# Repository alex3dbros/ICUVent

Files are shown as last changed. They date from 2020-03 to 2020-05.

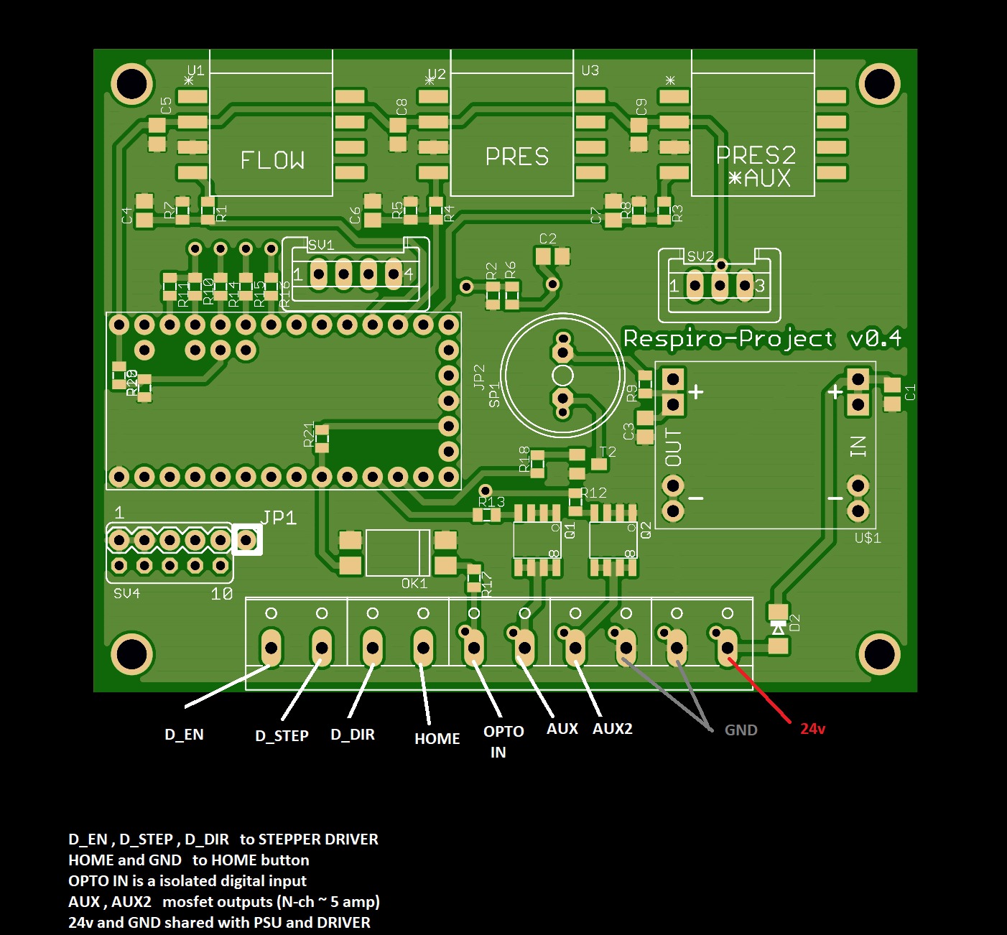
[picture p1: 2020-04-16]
Hardware/pinout.jpeg

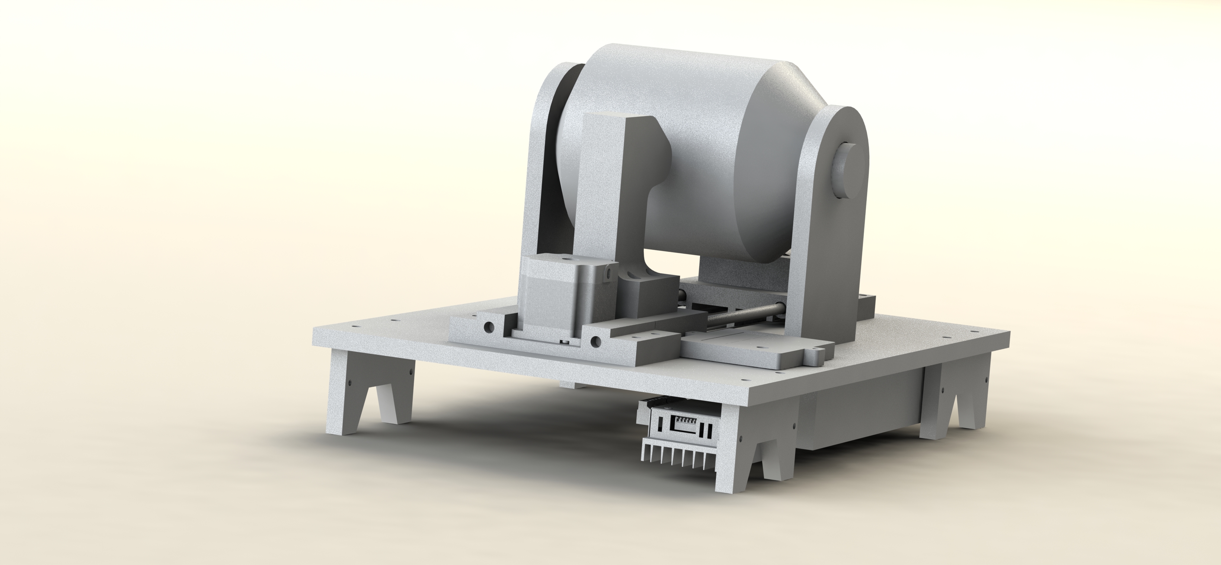
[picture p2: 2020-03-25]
3DModels/Render2.JPG

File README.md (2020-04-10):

# ICUVent

Video Overview: https://youtu.be/w7vbeYg_BhQ

This project is opensource and there are no guarantees given that this device 
will perform the actions that it's needed to be. Please use it with care and 
under the surveilance of professionals.

Project Structure:

Inside 3DModels folder you have the solidworks 2019 and STL files 
Inside programming you will have the programming code used to control the device.
We started with Arduino Nano, stepper Driver and nema 23 motor.

You have the schematics of the circuit attached as well.

Parts used that must be purchased: 

Mechanics:
4 x 8mm round bearings from 3d printer
2 x 8mm rods
1 x Nema 34 Motor // Updated from nema 23, will update the design soon.
1 x 16 mm T5 belt
2 x 18 teeth T5 gear
1 x Ambubag, preferable with PEEP valve and safety valve

Electronics: 
1 x Teensy 3.2
1 x Driver PSD8079-2P
1 x Encoder like this : https://www.amazon.com/Cylewet-Encoder-Digital-Potentiometer-Arduino/dp/B07DM2YMT4/ref=sr_1_6?keywords=encoder&qid=1585150874&sr=8-6
1 x DC to DC 24V to 5V like this : https://www.amazon.com/6-5-28V-MP1584-DC-DC-Step-Down-Module/dp/B082957QHR/ref=sr_1_3?keywords=MP1584+5V&qid=1585150582&sr=8-3
1 x 24 V Power supply
1 x EndStop switch
1 x raspberry pi with 7 inch display
1 x MPXV5004DP
1 x MPXV5010DP

Connection pins - https://www.amazon.com/Hotop-Pack-Single-Header-Connector/dp/B06XR8CV8P/ref=sr_1_1?keywords=2.54+pins&qid=1585151123&sr=8-1&swrs=BA6CC27AC84D7760BA1186A07738C3A9

https://www.amazon.com/DEYUE-Jumper-Wires-Set-breadboard/dp/B07LFCLMGW/ref=sr_1_10?keywords=jumper+wires&qid=1585151157&sr=8-10

Connection wires

Some info about how I built it:

I 3D printed parts and cut at the CNC the larger ones.
Here's a video with the machine functional

All the best!

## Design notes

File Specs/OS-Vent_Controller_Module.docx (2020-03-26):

Open Source Ventilator

Controller Module

V1.0; Sem Lampotang, March 17, 2020; Department of Anesthesiology, Center for Safety, Simulation & Advanced Learning Technologies, University of Florida, Gainesville, Florida, USA

This module is essentially a timer that turns two valves on or off. When the inspiratory valve is open, the exhalation valve is closed and vice versa.

Respiratory rate (RR) = Number of breaths per minute (bpm)

Breath duration = 60 s/RR; e.g., for 10 bpm, breath duration = 60/10 = 6 s

Inspiratory:Expiratory time ratio (I:E ratio) = 1:2 (usually)

Inspiratory time (Ti; time in seconds spent in inspiration phase) = breath duration / (1 + I:E) = 6/(1+2) = 6/3 = 2 seconds

Expiratory time (Te; time in seconds spent in exhalation phase) = breath duration – inspiratory time = 6 - 2 = = 4 seconds

Tidal volume (VT) = volume of gas (ml) delivered during inspiration

For a constant flow inspiration, the flow rate to the patient is VT/(inspiratory time)

Input | Data Output | Physical output | Status
User selects tidal volume (see General Engineering Specifications) | | Gas flows towards patient during the selected inspiratory time
| | In constant flow design, gas flows to patient at a flow rate of VT/
User selects respiratory rate (see General Engineering Specifications) | Time when inspiration starts and ends | Time when gas starts flowing to patient Time when gas stops flowing to patient | Not claimed; No one working on it yet
| Time when exhalation starts and ends | Time when gas starts flowing from patient Time when gas stops flowing from patient | No one working on it yet ; No one working on it yet
Electromechanical design (no software)
User selects respiratory rate (see General Engineering Specifications) | Time when inspiration starts and ends | 12 V delivered to inspiratory valve 0 V to exhalation valve | No one working on it yet ; No one working on it yet
| Time when exhalation starts and ends | 12 V delivered to exhalation valve 0 V to inspiratory valve | No one working on it yet ; No one working on it yet
Electromechanical design (software)
User selection for tidal volume and respiratory rate (see General Engineering Specifications) | Variable “INSPIRATORY_VALVE_ON” is true when inspiration starts “INSPIRATORY_VALVE_ON” is false when inspiration ends | 12 V delivered to inspiratory valve 0 V to exhalation valve | No one working on it yet ; No one working on it yet
| Variable “EXHALATION_VALVE_ON” is true when exhalation starts “EXHALATION_VALVE_ON” is false when exhalation ends | 12 V delivered to exhalation valve 0 V to inspiratory valve | No one working on it yet ; No one working on it yet
Pneumatic Design – May require specialized parts that may be out of stock

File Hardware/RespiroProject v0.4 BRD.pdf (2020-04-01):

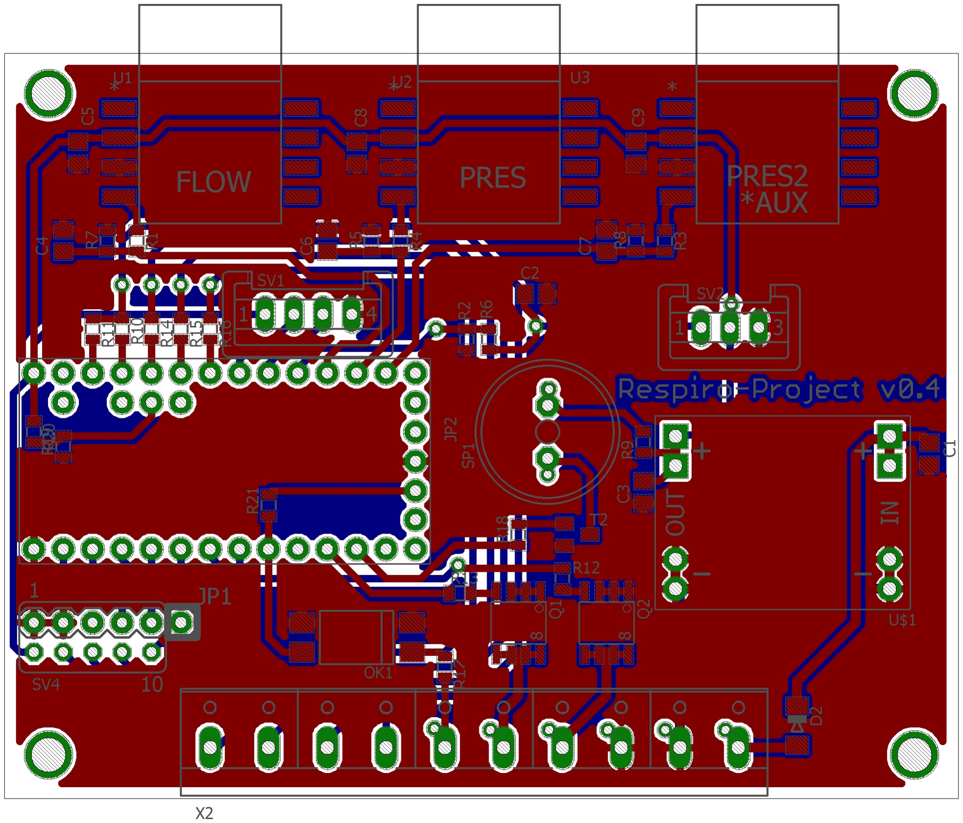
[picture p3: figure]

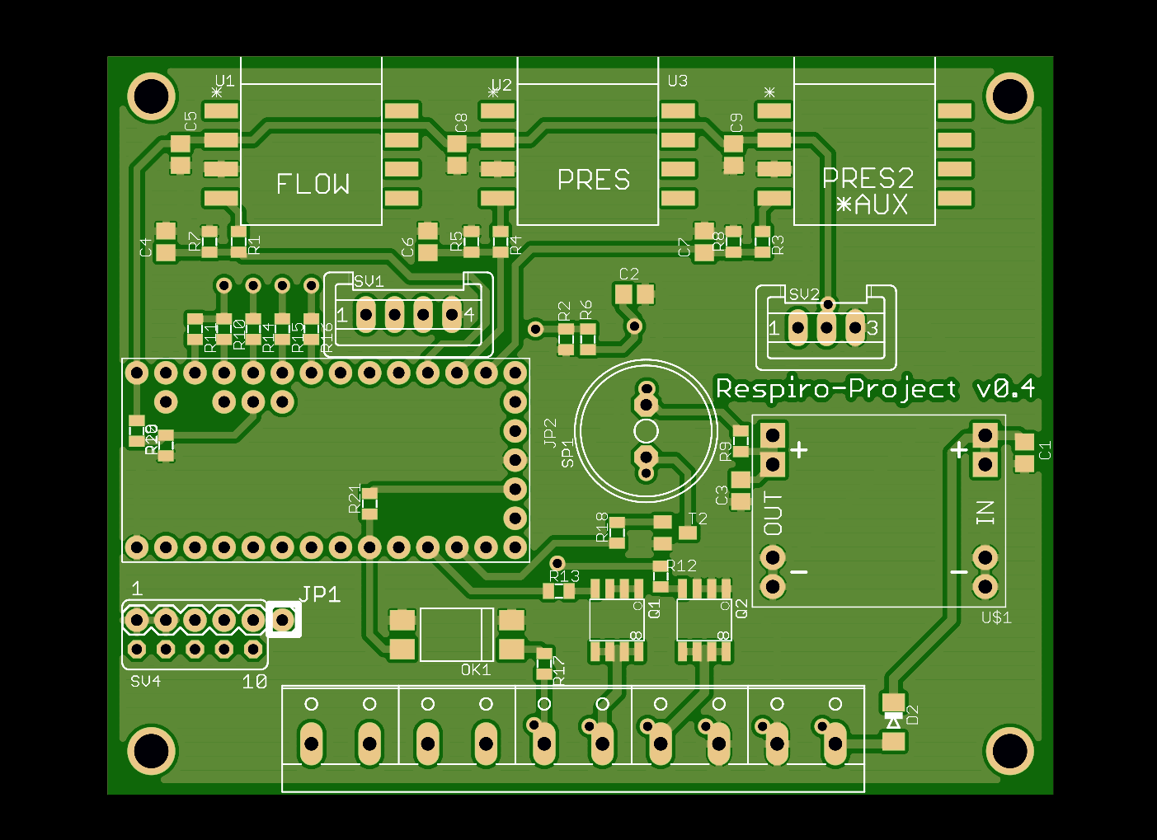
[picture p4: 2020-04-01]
Hardware/PCBPreview.png

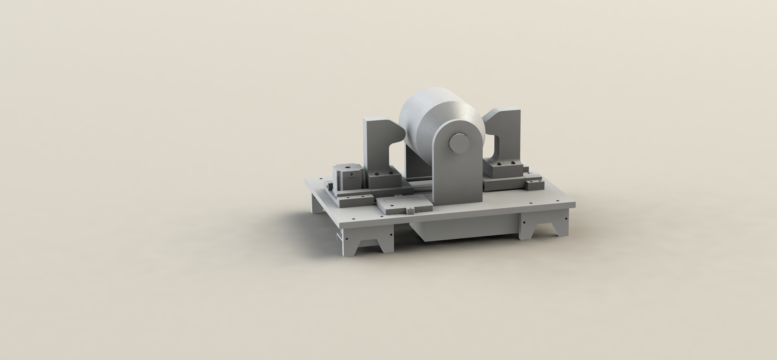
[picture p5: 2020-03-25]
3DModels/Render.JPG

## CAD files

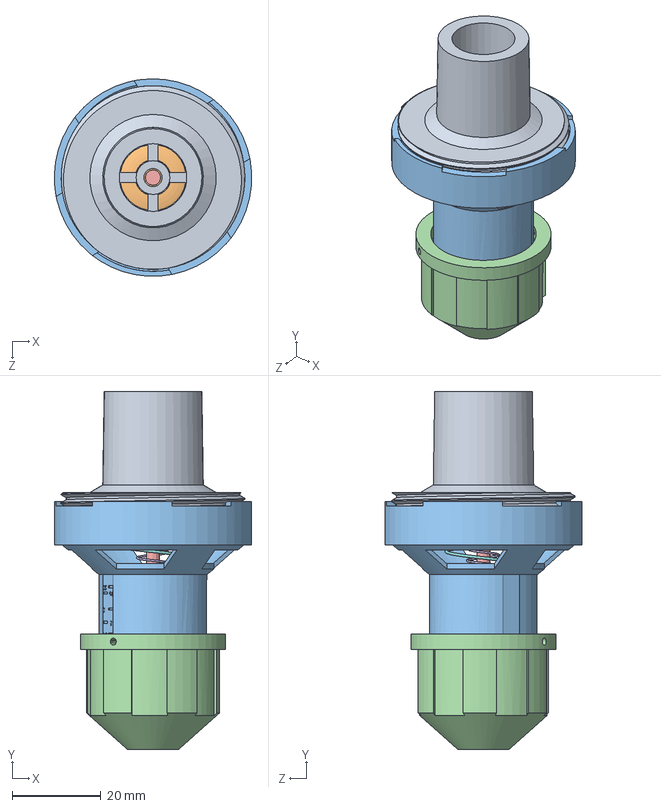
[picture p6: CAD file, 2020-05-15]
3DModels/Solidworks/ambu-bag-assembly-1.snapshot.2/Assy_PEEP_Valve.SLDASM
44.4 x 80.5 x 44.4 mm
PEEP_Body_Non_Adjustment
PEEP_Valve_Large_Silicone_Seal
PEEP_Body_Adjustment_Side
PEEP_Adjustment_Knob
PEEP_Pin_Center
PEEP_Spring_Taper
Platic_Float
PEEP_Spring_Large

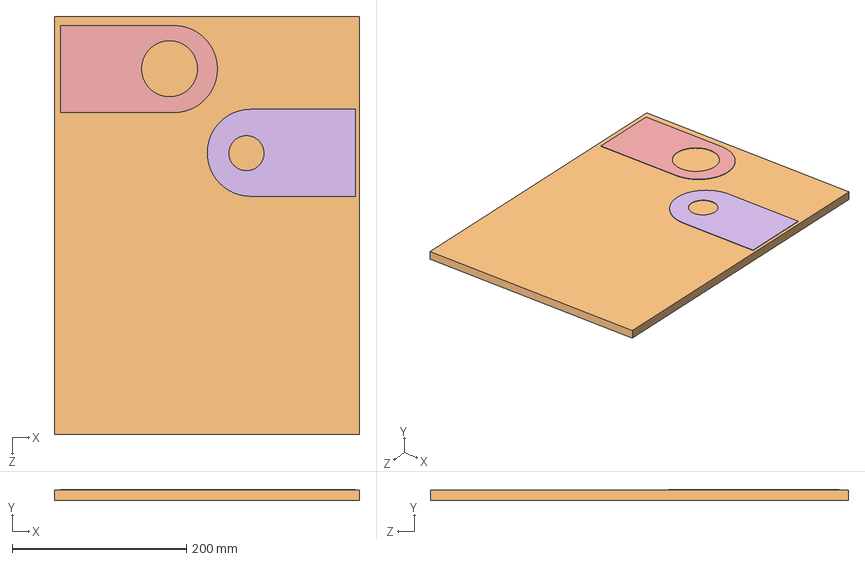
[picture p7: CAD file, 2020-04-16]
3DModels/Solidworks/CNC Cutting/CuttingParts_01.SLDASM
350.0 x 12.6 x 480.0 mm
MotorSupportNema34 x 4
StockMaterial
rolling_cnc_version x 4
GearSupport x 4
BagSupport1
BagSupport2

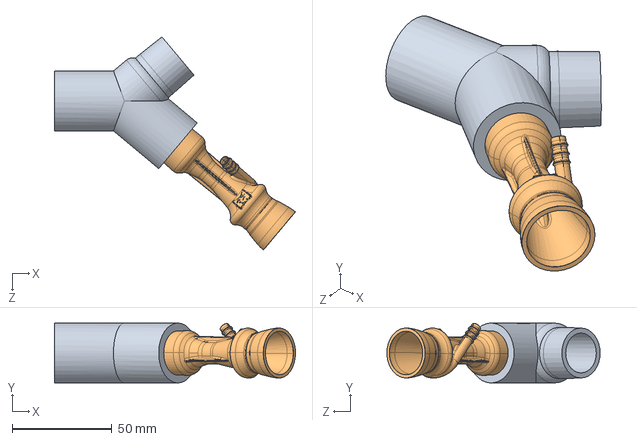
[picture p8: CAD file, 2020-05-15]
3DModels/Solidworks/Oxygen Mixing/Assem1.SLDASM
120.7 x 30.0 x 106.8 mm
Y_Oxygen_Connector
Respirator-free reanimation Venturi's valve (rev. 4) FiO2-40 Vertical, 1-piece

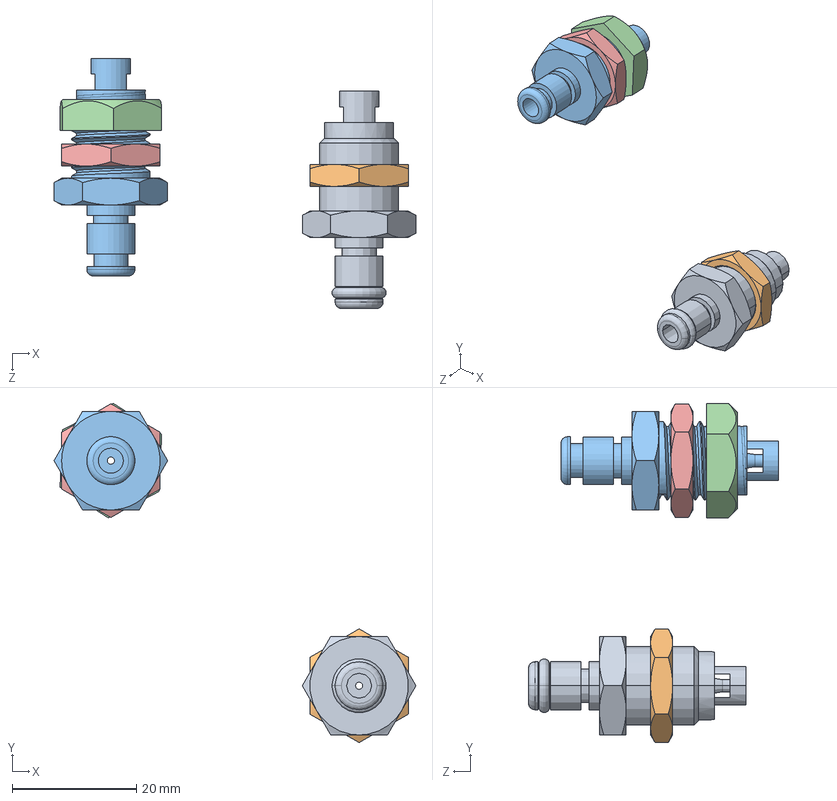
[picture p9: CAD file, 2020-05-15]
Fan Version/3D Models/Connectors/COLDER_PMC4201/SOLIDWORKS/PMC4201.sldasm
58.3 x 54.7 x 40.3 mm
_PMC4201_BODY_2
Nut
Nut2

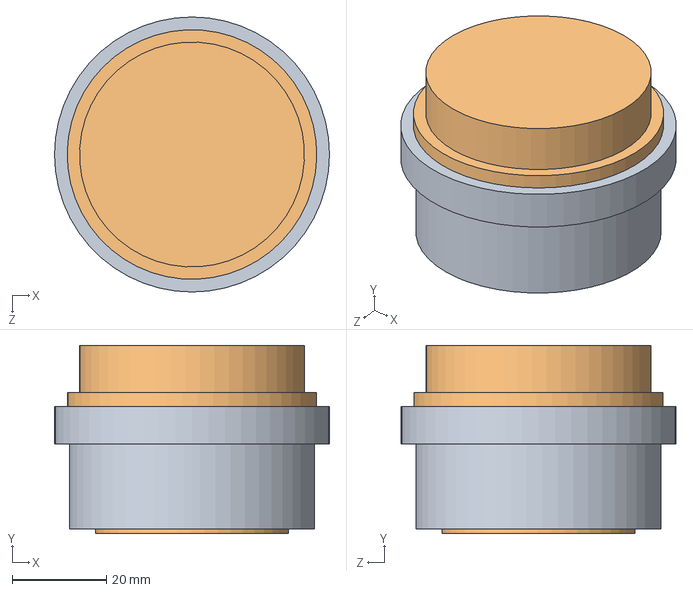
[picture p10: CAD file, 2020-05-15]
Fan Version/3D Models/Connectors/O2/O2.SLDASM
58.4 x 40.0 x 58.4 mm
O2Screw
R-30VSLDPRT

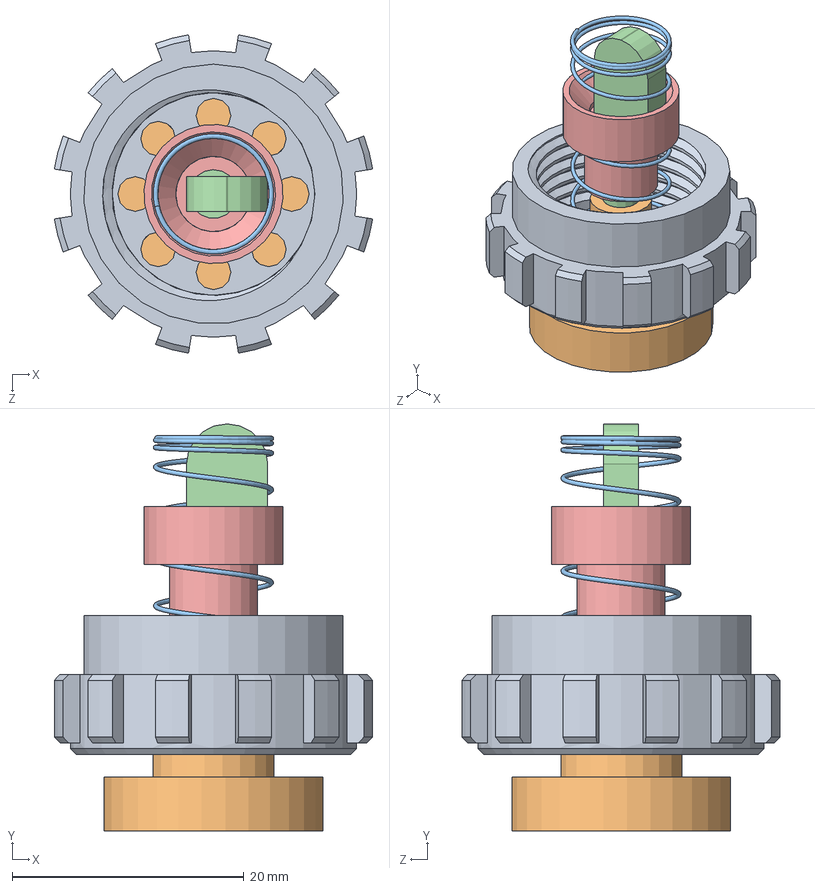
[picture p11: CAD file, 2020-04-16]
3DModels/Solidworks/ambu-bag-assembly-1.snapshot.2/Assy_Pressure_Relief_Valve.SLDASM
27.5 x 35.1 x 27.5 mm
Pressure Relief Valve Body
Pressure Relief Valve Pop_Up
Pressure Relief Valve Spring
Pressure Relief Valve Pin Center
Pressure Relief Valve Seal

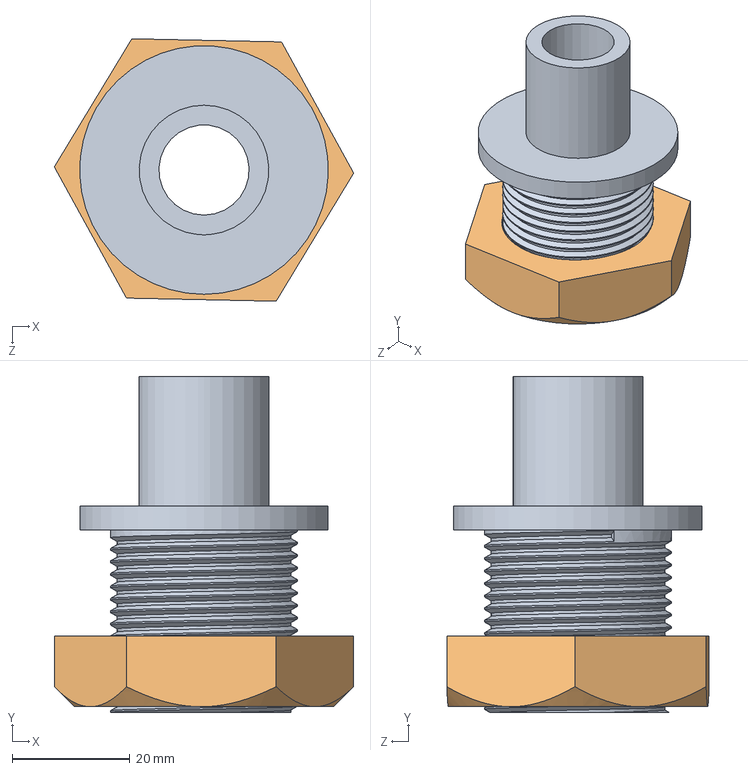
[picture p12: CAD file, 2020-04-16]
3DModels/Solidworks/OutputConnector.SLDASM
50.8 x 57.0 x 44.5 mm
OutputConnector-Screw
OutputConnector-Nut

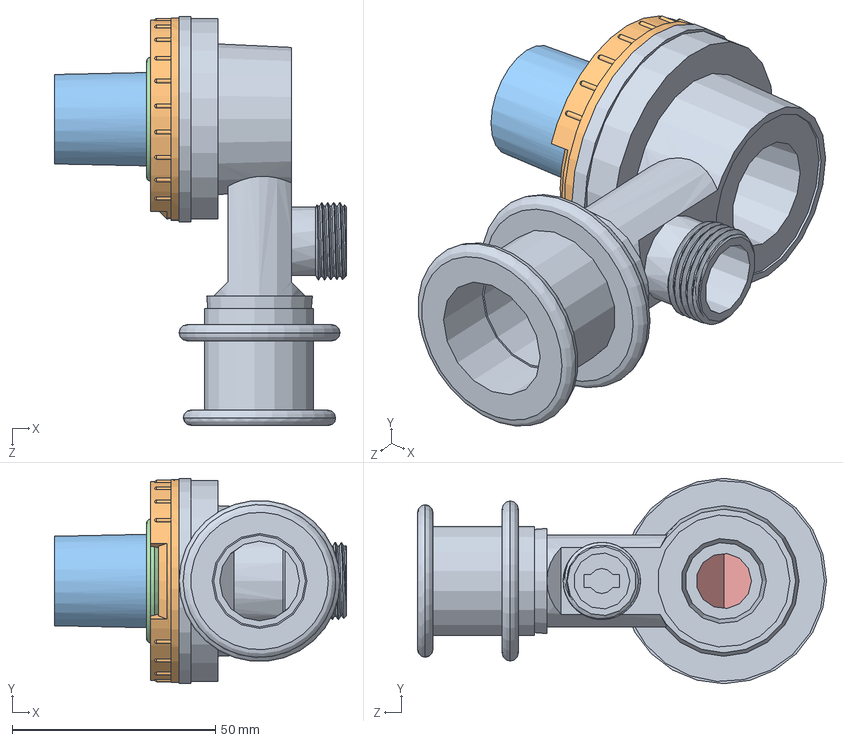
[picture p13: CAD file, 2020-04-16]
3DModels/Solidworks/ambu-bag-assembly-1.snapshot.2/Assy_Ambu-Bag_Outlet.SLDASM
71.8 x 50.5 x 100.6 mm
Ambu-Bag_Outlet
Ambu-Bag_Outlet_Body_Connector
Ambu-Bag_Outlet_Body_Connector_Pipe
Ambu-Bag_Outlet_Clip
Ambu-Bag_Outlet_Diaphram

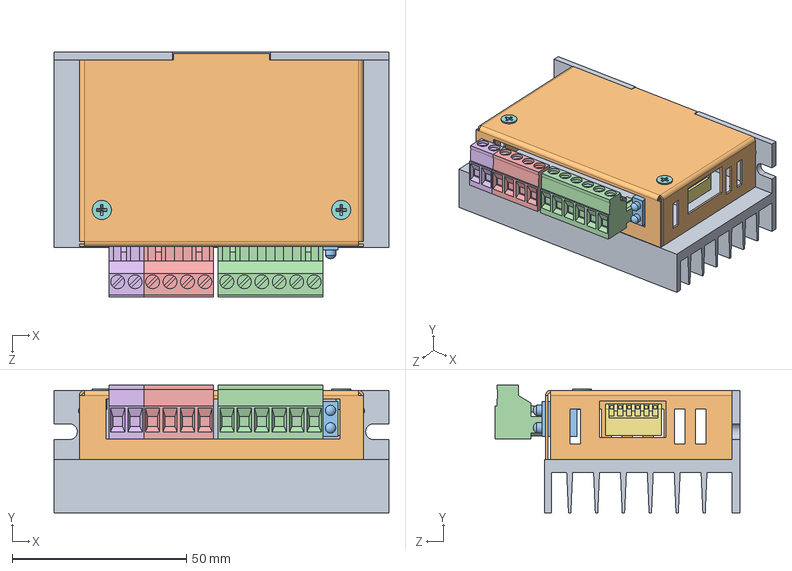
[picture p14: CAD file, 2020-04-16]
3DModels/Solidworks/SMAKN TB6600 STEPPER MOTOR DRIVER.SLDASM
96.0 x 36.6 x 70.3 mm
HEATSINK STYLE MOUNTING PLATE, SMAKN TB6600 STEPPER MOTOR DRIVER
SHEET METAL ENCLOSURE, SMAKN TB6600 STEPPER MOTOR DRIVER
LED BODY, SMAKN TB6600 STEPPER MOTOR DRIVER
EUROSTYLE TERMINAL BLOCK 6 POS 5.0 MM RA PLUG, SMAKN TB6600 STEPPER MOTOR DRIVER
EUROSTYLE TERMINAL BLOCK 4 POS 5.0 MM RA PLUG, SMAKN TB6600 STEPPER MOTOR DRIVER
EUROSTYLE TERMINAL BLOCK 2 POS 5.0 MM RA PLUG, SMAKN TB6600 STEPPER MOTOR DRIVER
DIP SWITCH, SMAKN TB6600 STEPPER MOTOR DRIVER
flat head screw_am x 2

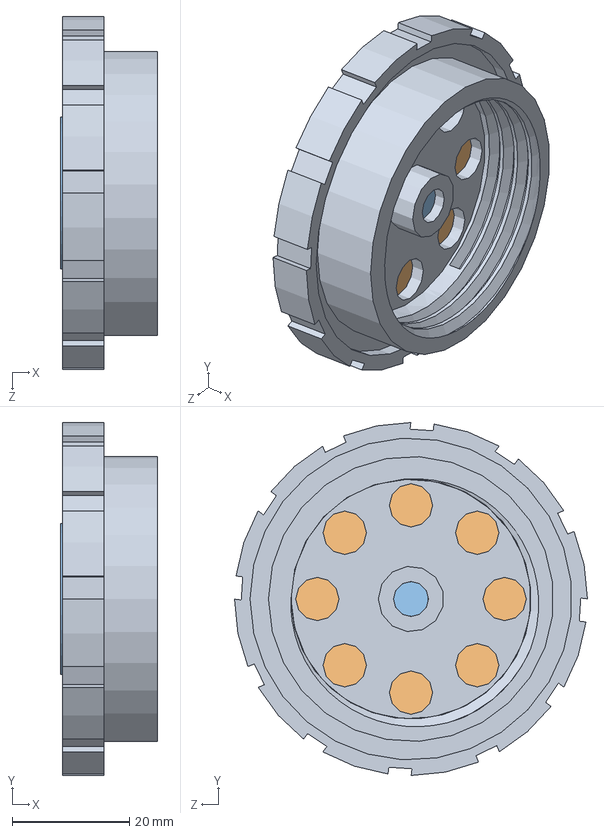
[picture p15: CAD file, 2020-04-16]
3DModels/Solidworks/ambu-bag-assembly-1.snapshot.2/Assy_Ambu-Bag_Inlet_Inner.SLDASM
16.6 x 60.3 x 60.3 mm
Ambu-Bag_Inlet_Inner
Ambu-Bag_Inlet_Inner_Seal
Ambu-Bag_Inlet_Inner_Flange

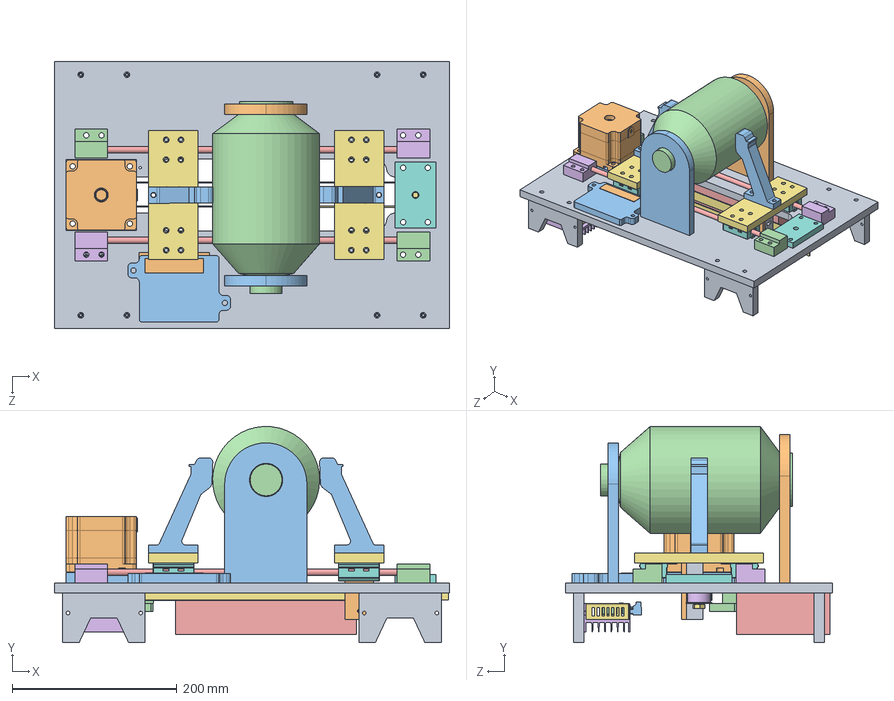
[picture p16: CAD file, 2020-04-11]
3DModels/Solidworks/ICUVent.SLDASM
480.0 x 262.5 x 325.0 mm
Base
BagSupport1
BagSupport2
ambubag
rod x 2
RodHolder x 2
belt x 2
Legs x 4
LimitSwitch
HEATSINK STYLE MOUNTING PLATE, SMAKN TB6600 STEPPER MOTOR DRIVER
SHEET METAL ENCLOSURE, SMAKN TB6600 STEPPER MOTOR DRIVER
LED BODY, SMAKN TB6600 STEPPER MOTOR DRIVER
EUROSTYLE TERMINAL BLOCK 6 POS 5.0 MM RA PLUG, SMAKN TB6600 STEPPER MOTOR DRIVER
EUROSTYLE TERMINAL BLOCK 4 POS 5.0 MM RA PLUG, SMAKN TB6600 STEPPER MOTOR DRIVER
EUROSTYLE TERMINAL BLOCK 2 POS 5.0 MM RA PLUG, SMAKN TB6600 STEPPER MOTOR DRIVER
DIP SWITCH, SMAKN TB6600 STEPPER MOTOR DRIVER
flat head screw_am x 2
RoulmentBeltTensing x 2
formed hex screw_am
hex nut jam_am
hex nut style 1_am
NEMA34-JK86HS68-5904
MotorSupportNema34
SwitchRaiser
Aluminium Gear re
Aluminium Gear re_tensioner
rolling_cnc_version x 2
SC8UU x 4
BeltGrabber
BeltGrabber_Tigthener
Pusher_Alumn x 2
RodHolder_mirror x 2

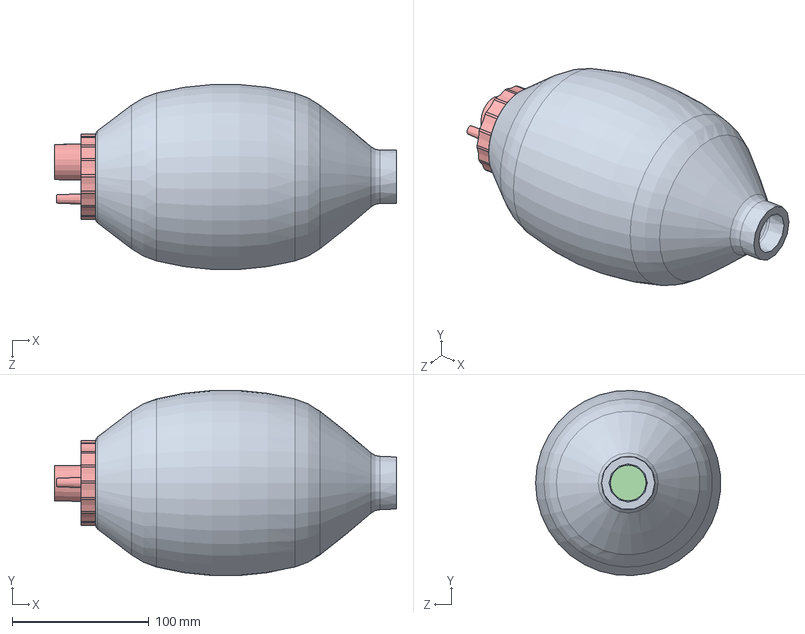
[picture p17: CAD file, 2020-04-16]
3DModels/Solidworks/ambu-bag-assembly-1.snapshot.2/Assy_Ambu-Bag.SLDASM
249.9 x 135.2 x 135.1 mm
Ambu-Bag_Bellows
Ambu-Bag_Inlet_Inner
Ambu-Bag_Inlet_Inner_Seal
Ambu-Bag_Inlet_Inner_Flange
Ambu-Bag_Inlet_Outer_Seal

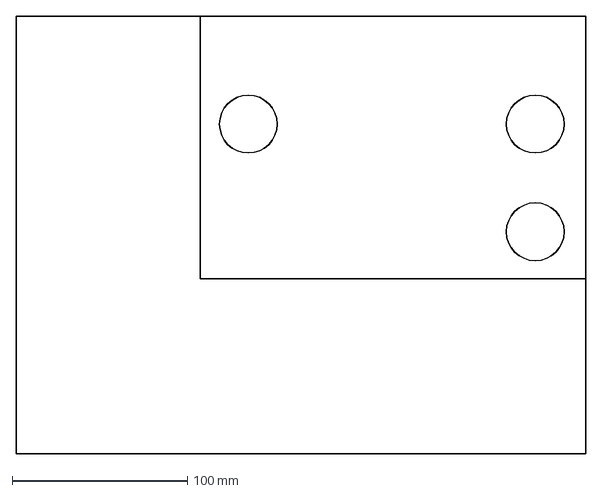
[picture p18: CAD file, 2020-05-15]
3DModels/CAD/LeftSide_template.DXF
325.0 x 250.0 mm

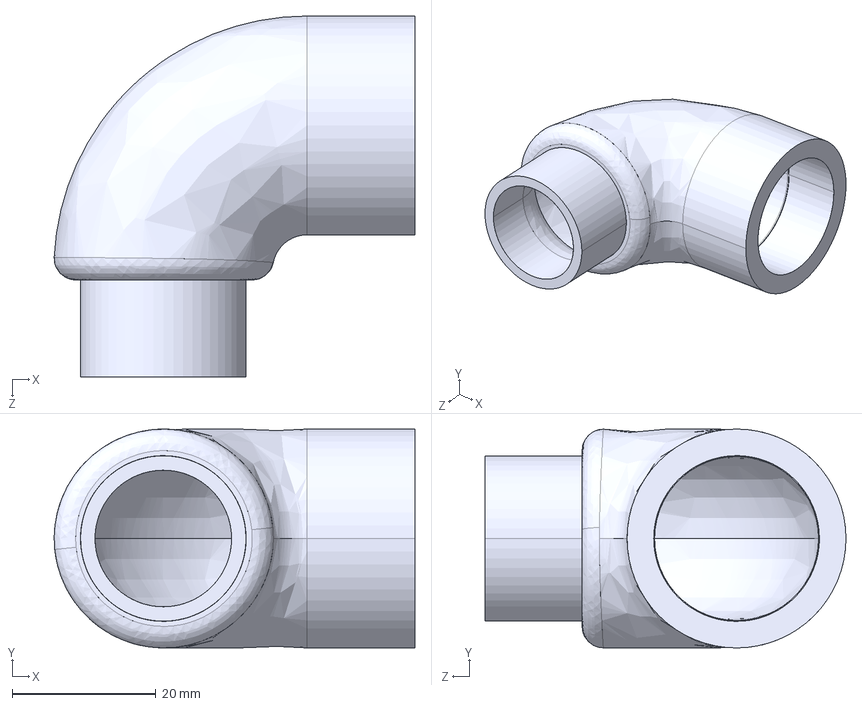
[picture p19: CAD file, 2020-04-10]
3DModels/IGS/tubes/90DegElbow_01.IGS
50.2 x 30.5 x 50.2 mm

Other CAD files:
3DModels/Solidworks/23mm-to-16mm-hose adapter.SLDPRT
3DModels/Solidworks/Case/LeftSide.SLDPRT
3DModels/Solidworks/ControllerSupport/ControllerSupport.SLDPRT
3DModels/Solidworks/Display Holding/DisplayBracket.SLDPRT
3DModels/CAD/BackAccessHole.DXF
3DModels/CAD/BagSupport1.DXF
3DModels/CAD/BagSupport2.DXF
3DModels/CAD/Base.DXF
3DModels/CAD/DisplayLid.DXF
3DModels/CAD/GearSupport.DXF
3DModels/CAD/MotorSupportNema34.DXF
3DModels/CAD/SwitchRaiser.DXF
3DModels/CAD/rolling_cnc_version.DXF
3DModels/Drawings/Base.SLDDRW
3DModels/IGS/Aluminium Gear re.IGS
3DModels/IGS/Aluminium Gear re_tensioner.IGS
3DModels/IGS/BagSupport1.IGS
3DModels/IGS/BagSupport2.IGS
3DModels/IGS/Base.IGS
3DModels/IGS/BeltGrabber.IGS
3DModels/IGS/BeltGrabber_Tigthener.IGS
3DModels/IGS/GearSupport.IGS
3DModels/IGS/MotorSupportNema34.IGS
3DModels/IGS/Pusher_Alumn.IGS
3DModels/IGS/RodHolder.IGS
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

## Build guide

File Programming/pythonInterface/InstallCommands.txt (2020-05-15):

QTPY: 
sudo apt-get install python3-qt5-default
sudo apt-get install python3-pyqt5
python3 -m pip install qtpy
python3 -m pip install pythongraph
python3 -m pip install qtmodern
python3 -m pip install scipy
sudo apt-get install libatlas-base-dev

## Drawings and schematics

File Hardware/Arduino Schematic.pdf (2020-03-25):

# 24 to 5V DC to DC

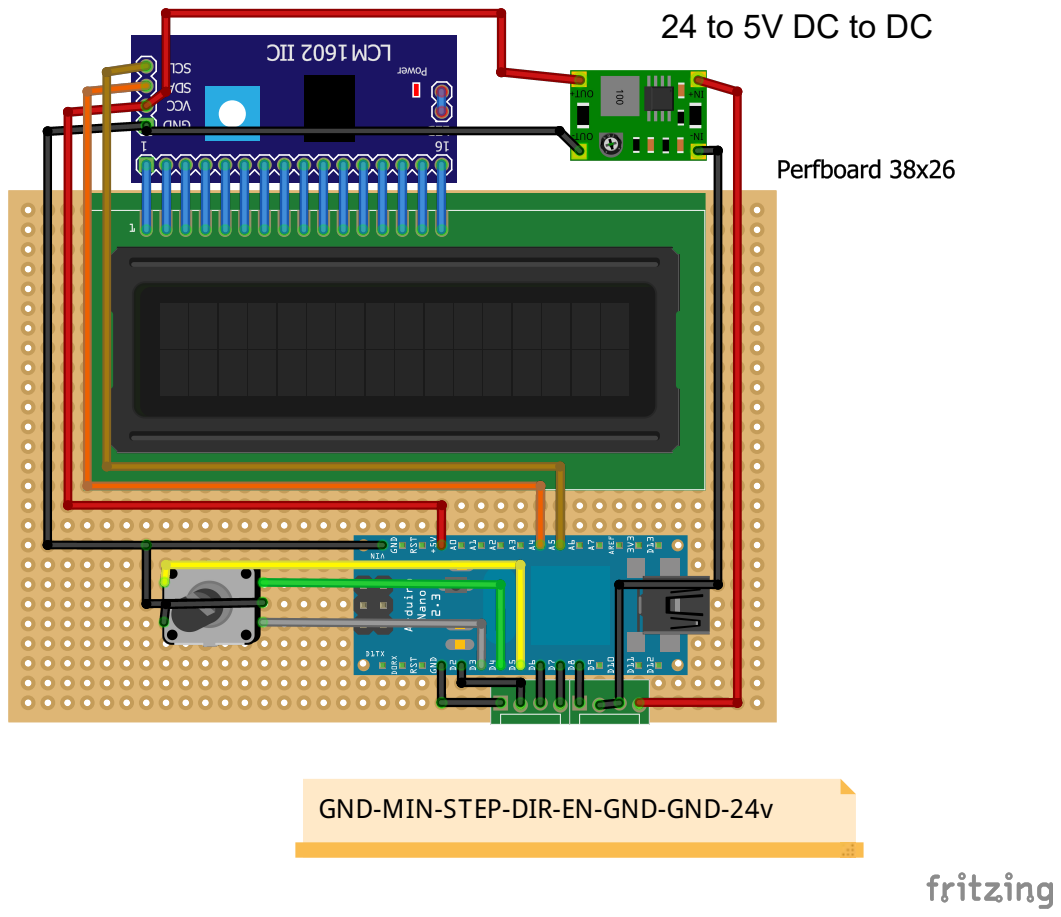
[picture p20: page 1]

GND-MIN-STEP-DIR-EN-GND-GND-24v

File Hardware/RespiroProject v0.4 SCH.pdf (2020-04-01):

# 100nf ¹K 1K 1K 1K 1K 1K

# C7 R¹ R³ R⁴ R⁵ R⁷ R⁸

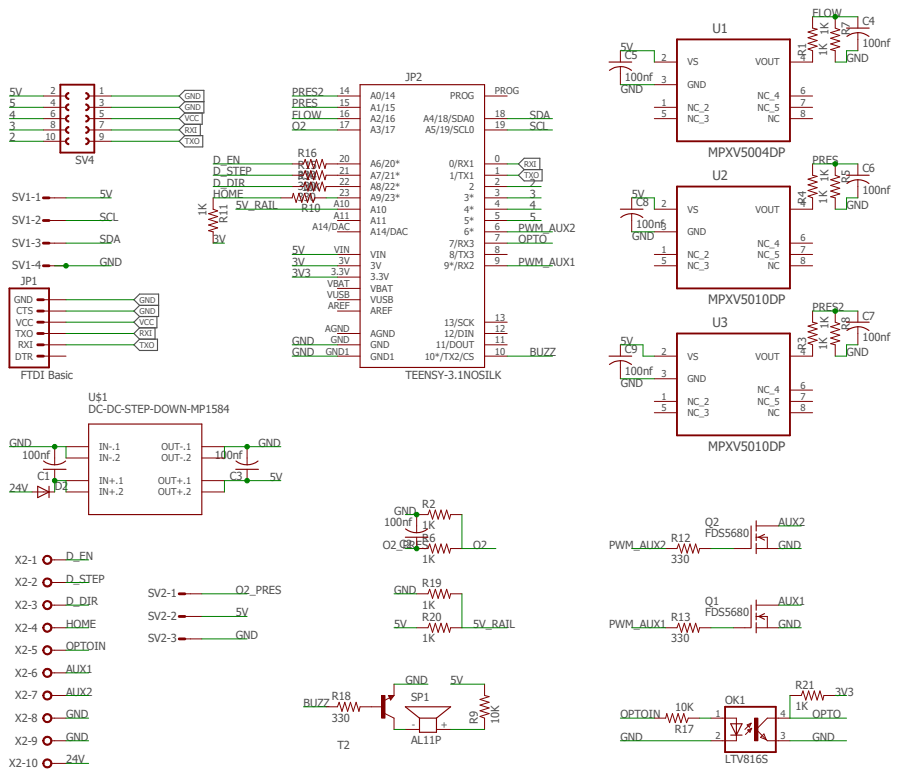
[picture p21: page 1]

DC-DC-STEP-DOWN-MP1584

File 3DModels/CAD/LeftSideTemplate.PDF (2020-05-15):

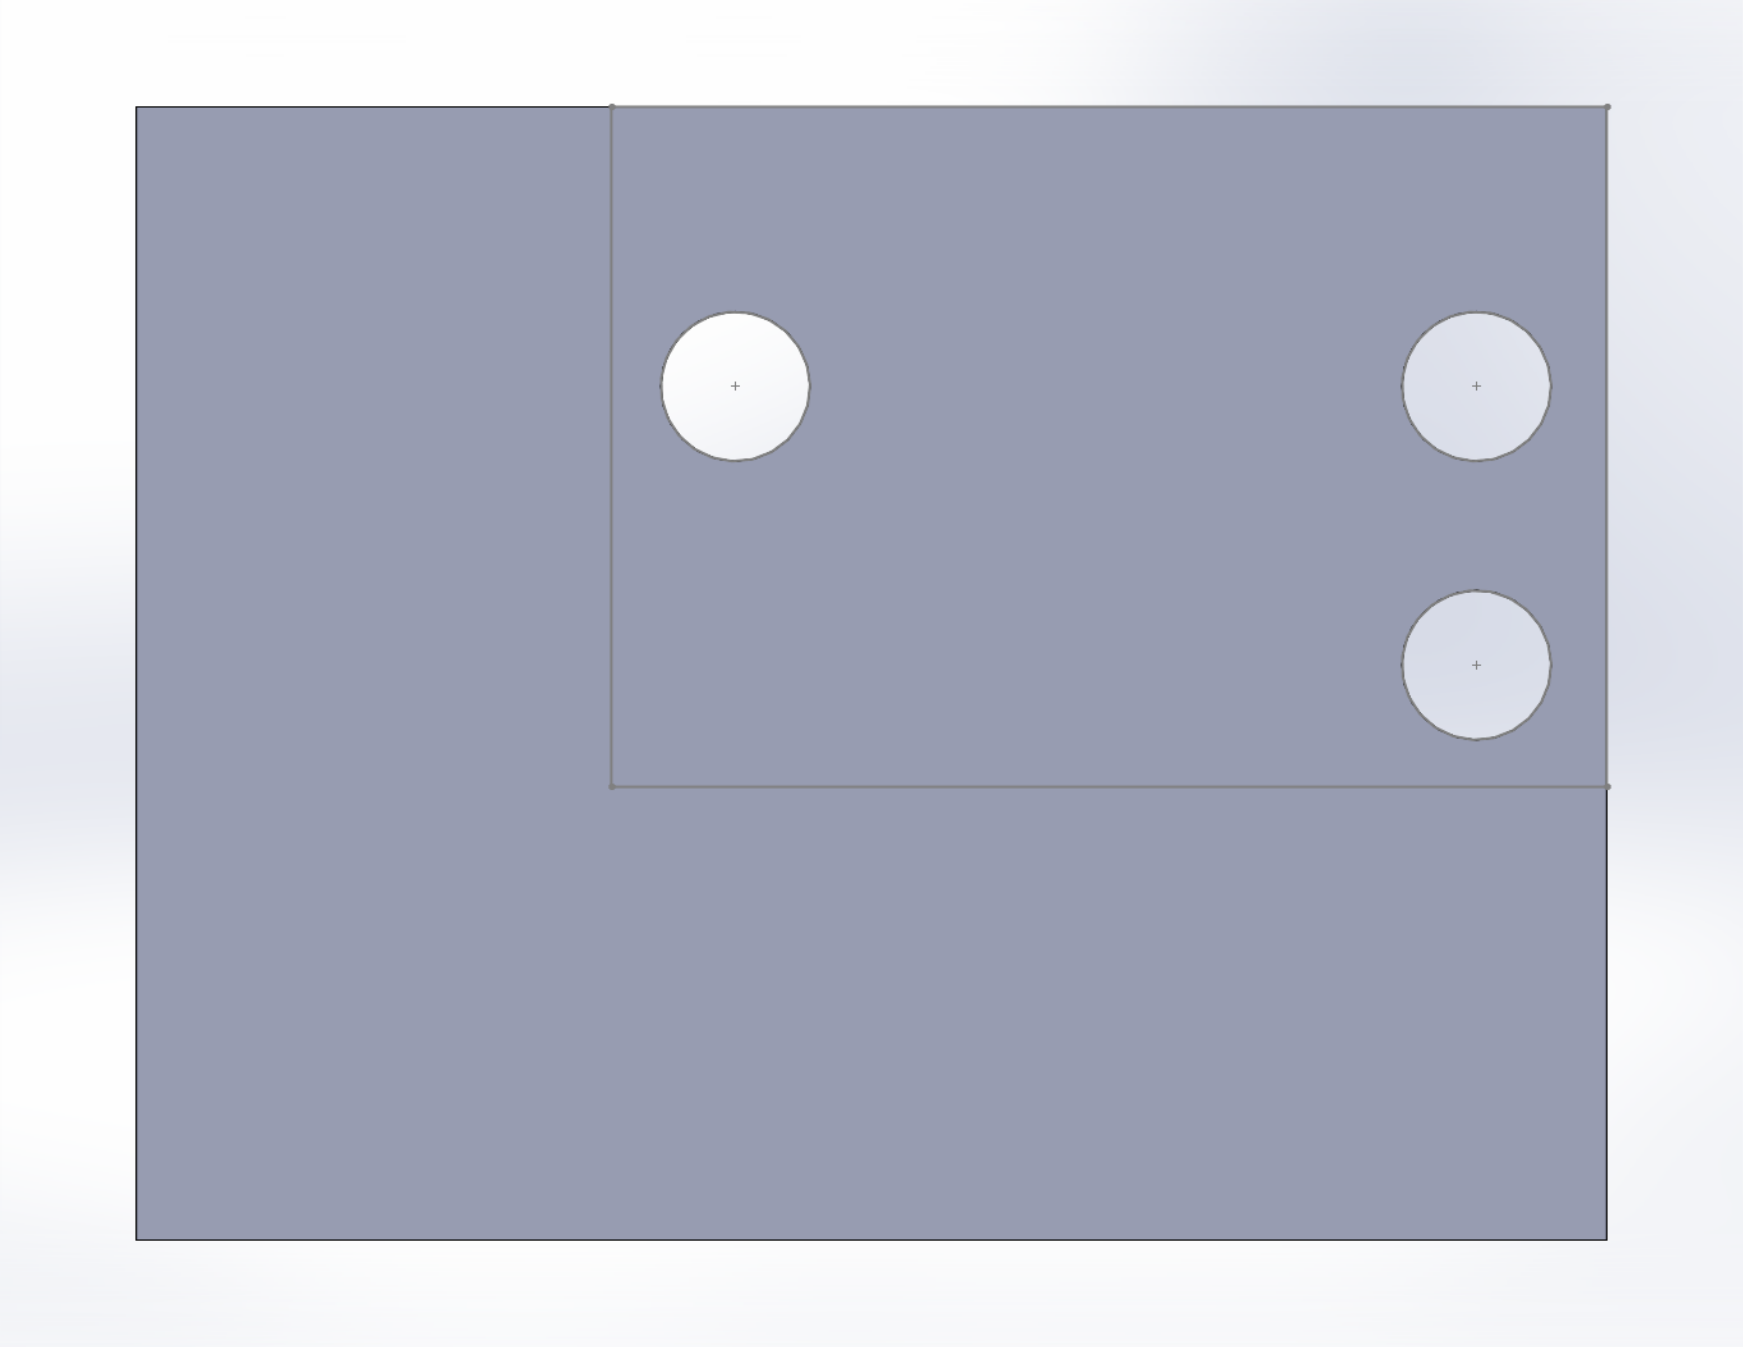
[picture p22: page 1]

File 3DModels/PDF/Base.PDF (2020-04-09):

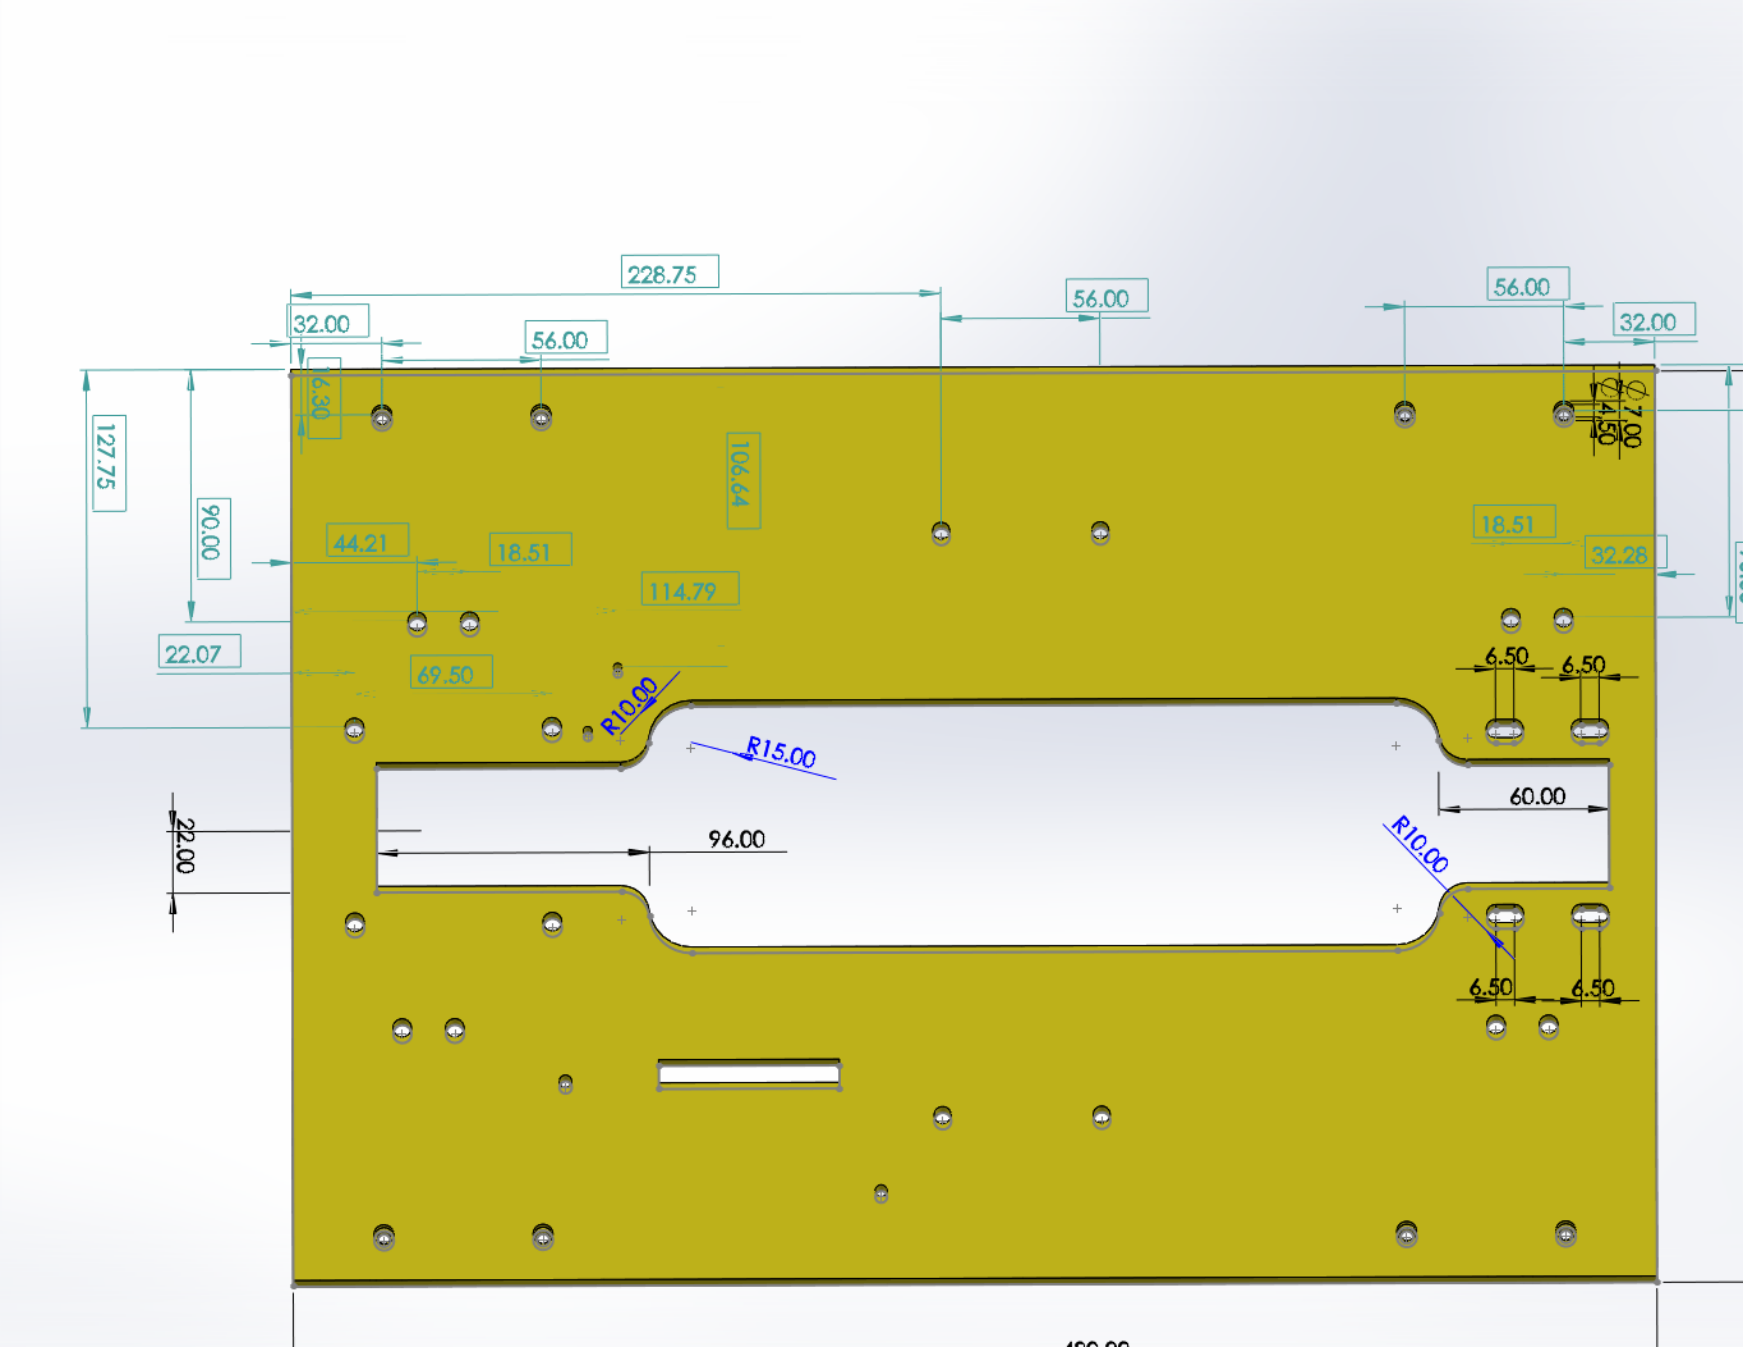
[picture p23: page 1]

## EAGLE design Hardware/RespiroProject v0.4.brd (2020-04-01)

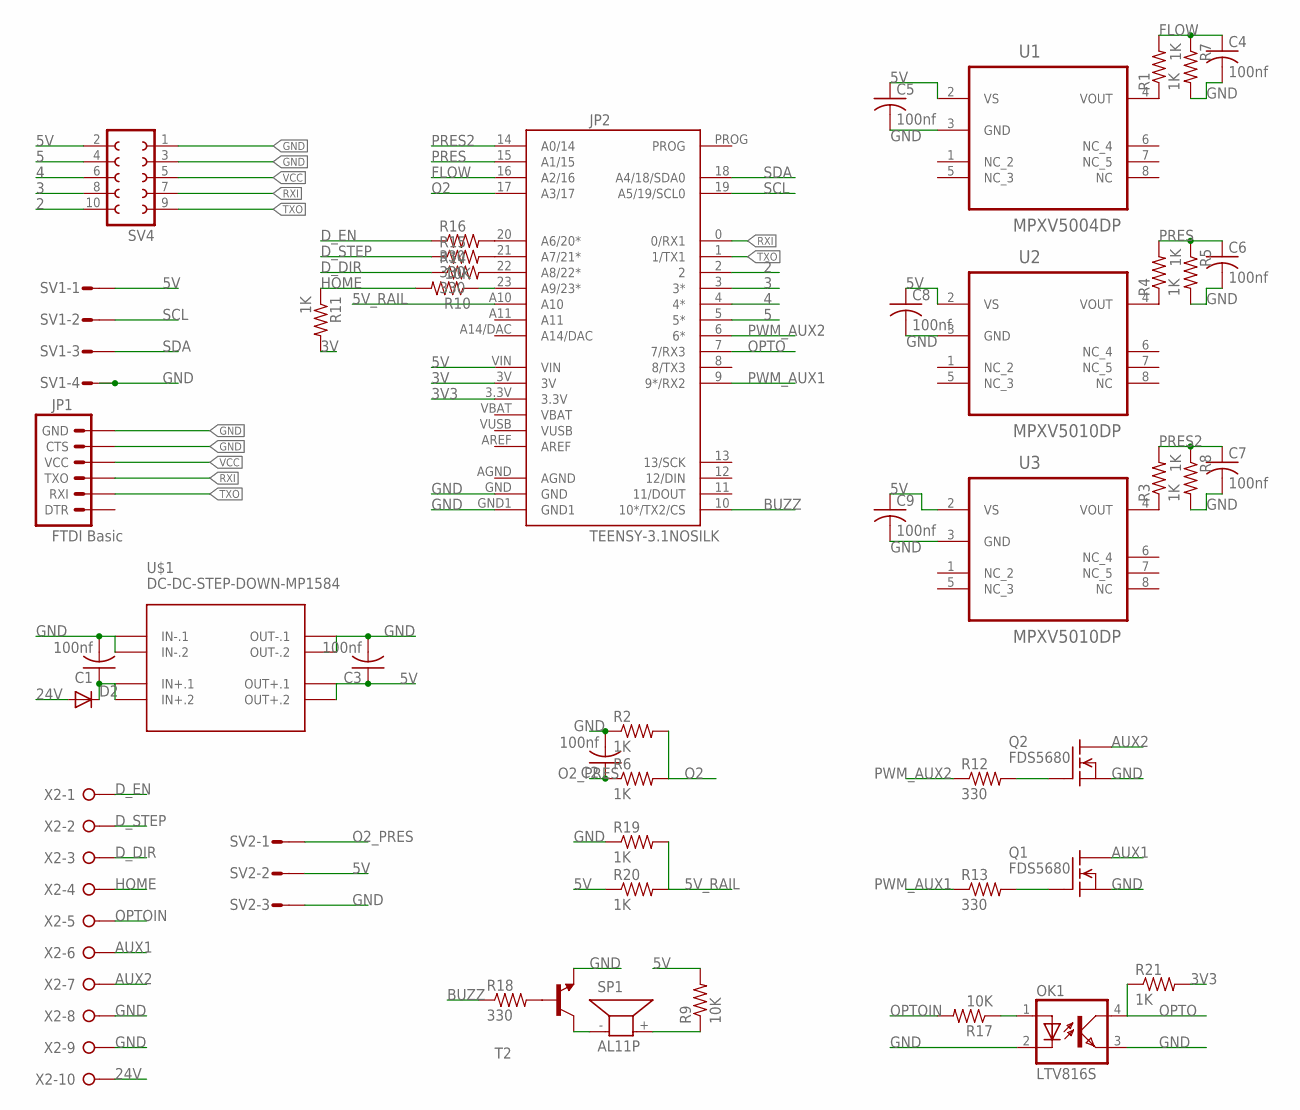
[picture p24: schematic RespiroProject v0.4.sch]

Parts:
C1, C2, C3, C4, C5, C6, C7, C8, C9: 100nf; C0805
D2: DIODE-MINIMELF; MINIMELF
JP1: FTDI Basic; 1X06
JP2: TEENSY-3.1NOSILK; TEENSY-3.1_NOSILK
OK1: LTV816S; DIL4-SMD
Q1, Q2: FDS5680; SO-8
R1, R2, R3, R4, R5, R6, R7, R8, R11, R19, R20, R21: 1K; 0805
R9, R10, R17: 10K; 0805
R12, R13, R14, R15, R16, R18: 330; 0805
SP1: AL11P
SV1: S04P
SV2: S03P
SV4: FE05-2
T2: BC817-16-NPN-SOT23-BEC; SOT23-BEC
U1: MPXV5004DP; FREESCALE_CASE_1351-01
U2, U3: MPXV5010DP; FREESCALE_CASE_1351-01
U$1: DC-DC-STEP-DOWN-MP1584
X2: W237-10P

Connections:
2: JP2.2, SV4.10
3: JP2.3 (3*), SV4.8
3V: JP2.3V, R11.2
3V3: JP2.3.3V, R21.2
4: JP2.4 (4*), SV4.6
5: JP2.5 (5*), SV4.4
5V: C3.1, C5.1, C8.1, C9.1, JP2.VIN, R9.2, R20.1, SV1.1, SV2.2, SV4.2, U1.2 (VS), U2.2 (VS), U3.2 (VS), U$1.OUT+.1, U$1.OUT+.2
5V_RAIL: JP2.A10, R19.2, R20.2
24V: D2.A, X2.10
AUX1: Q1.5 (D), Q1.6 (D), Q1.7 (D), Q1.8 (D), X2.6
AUX2: Q2.5 (D), Q2.6 (D), Q2.7 (D), Q2.8 (D), X2.7
BUZZ: JP2.10 (10*/TX2/CS), R18.1
D_DIR: R14.1, X2.3
D_EN: R16.1, X2.1
D_STEP: R15.1, X2.2
FLOW: C4.1, JP2.16 (A2/16), R1.2, R7.1
GND: C1.2, C2.2, C3.2, C4.2, C5.2, C6.2, C7.2, C8.2, C9.2, JP1.5 (CTS), JP1.6 (GND), JP2.GND, JP2.GND1, OK1.2 (C), OK1.3 (EMIT), Q1.1 (S), Q1.2 (S), Q1.3 (S), Q2.1 (S), Q2.2 (S), Q2.3 (S), R2.1, R5.2, R7.2, R8.2, R19.1, SV1.4, SV2.3, SV4.1, SV4.3, T2.E, U1.3 (GND), U2.3 (GND), U3.3 (GND), U$1.IN-.1, U$1.IN-.2, U$1.OUT-.1, U$1.OUT-.2, X2.8, X2.9
HOME: R10.2, R11.1, X2.4
unnamed: C1.1, D2.C, U$1.IN+.1, U$1.IN+.2
unnamed: R1.1, U1.4 (VOUT)
unnamed: R3.1, U3.4 (VOUT)
unnamed: R4.1, U2.4 (VOUT)
unnamed: SP1.- (1), T2.C
unnamed: R9.1, SP1.+ (2)
unnamed: JP2.23 (A9/23*), R10.1
unnamed: JP2.22 (A8/22*), R14.2
unnamed: Q2.4 (G), R12.2
unnamed: Q1.4 (G), R13.2
unnamed: JP2.21 (A7/21*), R15.2
unnamed: JP2.20 (A6/20*), R16.2
unnamed: OK1.1 (A), R17.1
unnamed: R18.2, T2.B
O2: JP2.17 (A3/17), R2.2, R6.2
O2_PRES: C2.1, R6.1, SV2.1
OPTO: JP2.7 (7/RX3), OK1.4 (COL), R21.1
OPTOIN: R17.2, X2.5
PRES: C6.1, JP2.15 (A1/15), R4.2, R5.1
PRES2: C7.1, JP2.14 (A0/14), R3.2, R8.1
PWM_AUX1: JP2.9 (9*/RX2), R13.1
PWM_AUX2: JP2.6 (6*), R12.1
RXI: JP1.3 (TXO), JP2.0 (0/RX1), SV4.7
SCL: JP2.19 (A5/19/SCL0), SV1.2
SDA: JP2.18 (A4/18/SDA0), SV1.3
TXO: JP1.2 (RXI), JP2.1 (1/TX1), SV4.9
VCC: JP1.4 (VCC), SV4.5

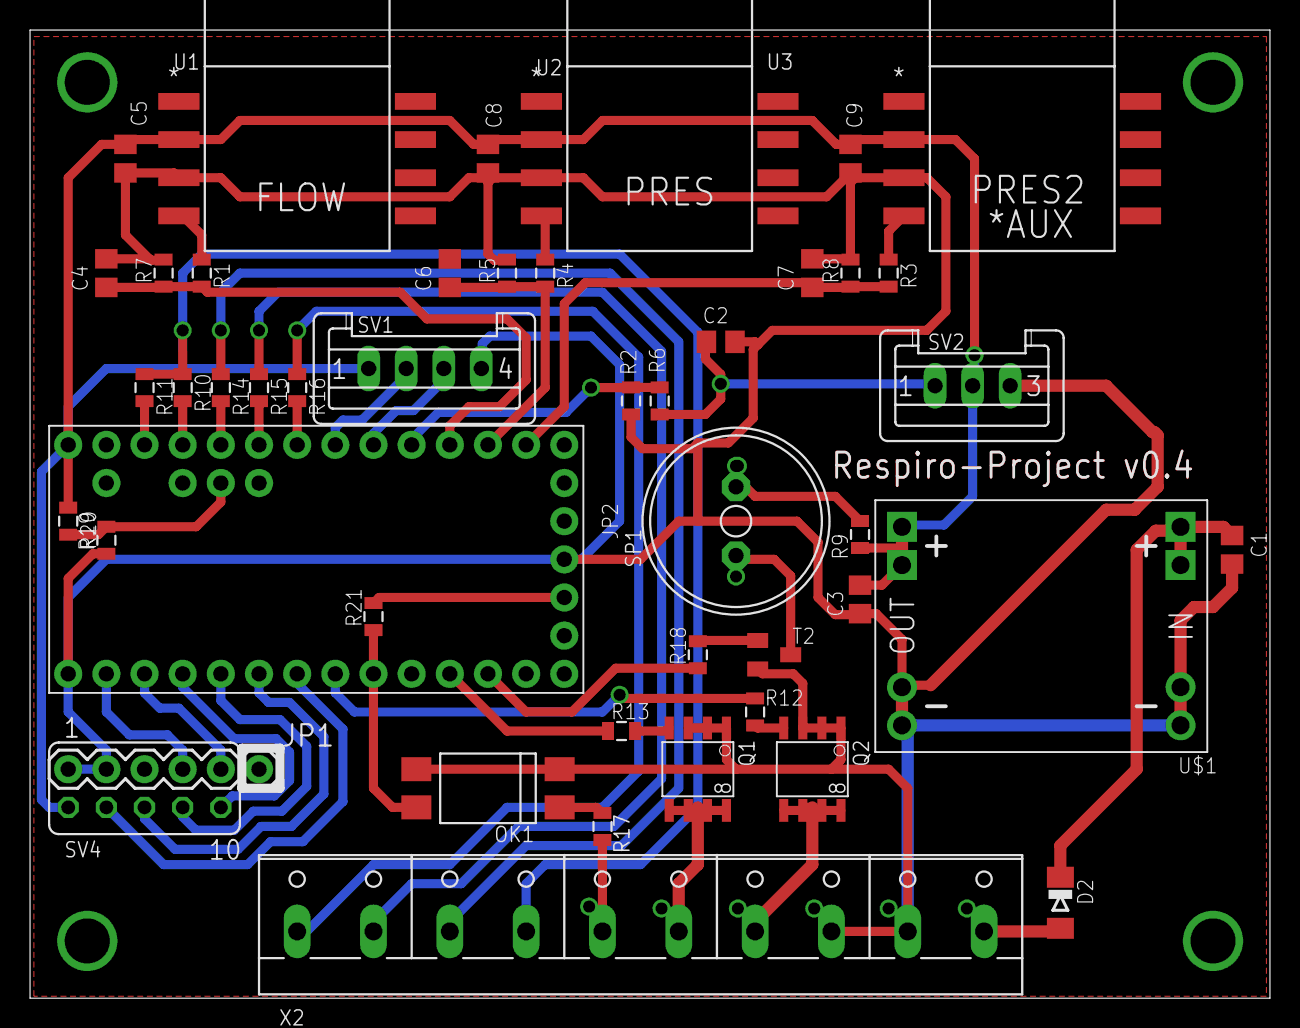
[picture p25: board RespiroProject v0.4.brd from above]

Board: 2 copper layers, 82.5 x 64.4 mm, 46 parts (0 on the bottom side), 45 nets.

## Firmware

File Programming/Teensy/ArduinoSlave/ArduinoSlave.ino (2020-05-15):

/*
 Name:		ArduinoSlave.ino
 Created:	3/25/2020 9:00:42 PM
 Author:	Alex Gradea
*/
#include <Arduino.h>
#include <ArduinoJson.hpp>
#include <ArduinoJson.h>
#include <EEPROM.h>
#include "EEPROMAnything.h"
#include <Wire.h> 
#include "TeensyStep.h"

#include <ADC.h>
#include <ADC_util.h>


#define HWSERIAL Serial1
int buttonState = 0;

const int readPin = A2; // ADC0
const int readPin2 = A1; // ADC1

ADC* adc = new ADC(); // adc object

// stepper and  controller
constexpr int stpPin = 21, dirPin = 22;
StepControl controller;    // Use default settings 
Stepper motor(stpPin, dirPin);

const int LED = 13;
volatile int readPressure = 1;
int ledState = LOW;
volatile unsigned long blinkCount = 0;

int millisbetweenSteps = 1;

#define ENdrv 20
#define ZERO_POS 23 // Endstop

long counter = 0;
int State;
int LastState;

int menu_page = 0;

int maxBreathsPM = 40;
int minBreathsPM = 3;

int maxAirVol = 600;
int minAirVol = 200;

int maxTimeBB = 100;
int minTimeBB = 0;

int maxInhaleRatio = 3;
int minInhaleRatio = 1;

long minMotionLength = 10;
long maxMotionLength = 15000; // hard limiting the movement of the mechanics

int homePosition = 150;
int offSwitchPos = 300;
int zeroed = 0;
int ventPos = 0;

int minStepperSpeed = 100;
int maxStepperSpeed = 10000;
int acceleration = 30000;

unsigned long last_watchdog_update = 0;
unsigned long last_sensorWatchdog_update = 0;

bool needInhale = true;
bool needExhale = false;

bool inhaling = false;
bool exhaling = false;
bool motorShouldRun = false;

String input;

float adcMultiplier = 0.1875;
int16_t readVal1, readVal2;


unsigned long lastDebug = 0;
unsigned long debugInhaleTime = 0;
unsigned long debugExhaleTime = 0;

struct config
{
	int breathsPerMinute;
	int airVol;
	int inhaleExhaleRatio;
	long motionLength;
	int stepperSpeed;
};

typedef struct config Config;
Config conf;

void setup() {

	motor.setMaxSpeed(maxStepperSpeed);
	motor.setAcceleration(acceleration);

	pinMode(readPin, INPUT);
	pinMode(readPin2, INPUT);
	pinMode(10, OUTPUT);
	digitalWrite(10, LOW);
	// Setting ADC0
	adc->adc0->setAveraging(32); // set number of averages
	adc->adc0->setResolution(16); // set bits of resolution
	adc->adc0->setConversionSpeed(ADC_CONVERSION_SPEED::HIGH_SPEED_16BITS); // change the conversion speed
	adc->adc0->setSamplingSpeed(ADC_SAMPLING_SPEED::VERY_HIGH_SPEED); // change the sampling speed

	pinMode(LED, OUTPUT);
	pinMode(ENdrv, OUTPUT);
	digitalWrite(ENdrv, LOW); // Stepper driver ENABLE ! 

	//Define the pins as inputs
	pinMode(ZERO_POS, INPUT_PULLUP);
	Serial.begin(9600);
	HWSERIAL.begin(115200); //Start serial com so we could print the value on the serial monitor

	loadOrwriteDefaults();

}

void loop() {

	if (!zeroed) {
		delay(100);
		zero_position();
		motorShouldRun = true;
		needInhale = true;
	}


	serialCom();
	
	unsigned long current_millis = millis();
	unsigned long lastPrint;

	
	float timeToInhale = getInhaleTime(conf.breathsPerMinute);
	float timeToExhale = getExhaleTime(conf.breathsPerMinute);




	sensorsWatchdog();

	if (needInhale || inhaling) {

		if (needInhale) {
			Serial.print("This should be inhale time: ");
			Serial.println(timeToInhale);

			debugInhaleTime = millis();

			setMotorSpeed(timeToInhale);
			setAirVolume();
			ventWatchdog(conf.motionLength, "Inhale");
			needInhale = false;
		}
		
		if (inhaling) {
			if (motor.getPosition() == conf.motionLength) {

				needExhale = true;
				inhaling = false;
				Serial.print("Time to inhale: ");
				Serial.println(current_millis - debugInhaleTime);

				//Serial.print("At stepper Speed: ");
				//Serial.println(conf.stepperSpeed);

			}

		}

	}


	if (needExhale || exhaling) {

		//Serial.println("I am getting here 1");

		if (needExhale) {
			debugExhaleTime = millis();
			//Serial.print("This should be exhale time: ");
			//Serial.println(timeToExhale);

			setMotorSpeed(timeToExhale);
			ventWatchdog(homePosition, "Exhale");
			needExhale = false;
		}

		if (exhaling) {
			//Serial.println("I am getting here 3");

			//Serial.print("This is motor Position: ");
			//Serial.println(motor.getPosition());

			if (motor.getPosition() == homePosition) {
				needInhale = true;
				exhaling = false;

				//Serial.println("Time to exhale: ");
				//Serial.println(current_millis - debugExhaleTime);

				//Serial.println("At stepper Speed: ");

				//Serial.println(conf.stepperSpeed);
				//Serial.println("");
				//Serial.println("");

			}

		}

	}


	// read the state of the pushbutton value:
	buttonState = digitalRead(23);

	// check if the pushbutton is pressed.
	// if it is, the buttonState is HIGH:
	if (buttonState == HIGH) {
		// turn LED on:    
		Serial.println("1");
	}
	else {
		// turn LED off:
		Serial.println("0");
	}





	if (motorShouldRun) {
		//ventMotor.run();
		homeSwitchCheck();
	}

	if (!motorShouldRun) {
		//ventMotor.stop();
	}
	


}

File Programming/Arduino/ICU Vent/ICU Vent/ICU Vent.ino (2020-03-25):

/*
 Name:		ICU_Vent.ino
 Created:	3/21/2020 2:37:30 PM
 Author:	Alex Gradea (3D-Brothers.SRL)
*/

#include <EEPROM.h>
#include "EEPROMAnything.h"

#include "Button2.h";

#include <Wire.h> 
#include <LiquidCrystal_I2C.h>
LiquidCrystal_I2C lcd(0x27, 16, 2);  // set the LCD address to 0x27 for a 16 chars and 2 line display

#include <Stepper.h>

#define STEPS 12800 // Number of steps per revolution
Stepper stepper(STEPS, 6, 7);
int millisbetweenSteps = 1;

#define ENdrv 8
#define clk 3
#define data 4

#define ZERO_POS 2 // Endstop
#define step_pin 6 // Pin 3 connected to Steps pin 
#define dir_pin 7  // Pin 2 connected to Direction pin

#define BUTTON_A_PIN  5
Button2 buttonA = Button2(BUTTON_A_PIN);

long counter = 0;
int State;
int LastState;

int menu_page = 0;

int maxBreathsPM = 40;
int minBreathsPM = 3;

int maxAirVol = 100;
int minAirVol = 10;

int maxTimeBB = 100;
int minTimeBB = 0;

long minMotionLength = 10;
long maxMotionLength = 2000;
int zeroed = 0;
int ventPos = 0;
int breathingSpdMult = 1500;

unsigned long last_watchdog_update = 0;
unsigned long last_display_update = 0;

String firstLine = "DIY Ventilator v1.0";
String secondLine = "Starting";

String firstLcdText = "";
String secondLcdText = "";
int needInhale = 1;
int needExhale = 0;

struct config
{
	int breathingSpeed;
	int airVol;
	int timeBetweenBreaths;
	int inhaleToExhale;
	long motionLength;
};

typedef struct config Config;
Config conf;


void loadOrwriteDefaults() {

	int canWriteDefaults;
	EEPROM_readAnything(80, canWriteDefaults);
	//canWriteDefaults = -1;

	if (canWriteDefaults == -1) {
		
		conf.breathingSpeed = 12;
		conf.airVol = 80;
		conf.timeBetweenBreaths = 0;
		conf.inhaleToExhale = 0;
		conf.motionLength = 5000;
		EEPROM_writeAnything(0, conf);
		EEPROM_writeAnything(80, 1);
	}

	if (canWriteDefaults == 1) {

		EEPROM_readAnything(0, conf);

	}
}


void setup() {

	pinMode(ENdrv, OUTPUT);
	digitalWrite(ENdrv, HIGH); // Stepper driver ENABLE ! 

    //Define the pins as inputs
	pinMode(clk, INPUT_PULLUP);
	pinMode(data, INPUT_PULLUP);
	pinMode(BUTTON_A_PIN, INPUT_PULLUP);
	pinMode(ZERO_POS, INPUT_PULLUP);

	buttonA.setClickHandler(ButtonHandler);
	buttonA.setLongClickHandler(ButtonHandler);

	Serial.begin(9600); //Start serial com so we could print the value on the serial monitor

	// Reads the initial state of the clock pin
	LastState = digitalRead(clk);

	lcd.init();                      // initialize the lcd 

	// Print a message to the LCD.
	lcd.backlight();
	lcd.setCursor(1, 0);
	lcd.print("DIY Ventilator v1.0");
	lcd.setCursor(5, 1);
	lcd.print("Starting");

	loadOrwriteDefaults();
	stepper.setSpeed(conf.breathingSpeed * breathingSpdMult);

}

void loop() {

	if (!zeroed) {
		delay(1000);
		zero_position();

	}
	displayControl();


	unsigned long current_millis = millis();

	if (current_millis - last_watchdog_update >= float(conf.timeBetweenBreaths) * 100 && needInhale)
	{
		
		ventWatchdog(conf.motionLength * (conf.airVol / 100.0));

		last_watchdog_update = millis();
		needInhale = 0;
		needExhale = 1;

	}

	current_millis = millis();

	if (current_millis - last_watchdog_update >= float(conf.inhaleToExhale) * 100 && needExhale) {

		ventWatchdog(20);

		needInhale = 1;
		needExhale = 0;
		
		last_watchdog_update = millis();

	}

}

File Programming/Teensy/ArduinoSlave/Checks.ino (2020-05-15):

void setBreathsPerMinuteParam(int numberOfBreaths) {

	int validNBreaths = hardLimiter(minBreathsPM, maxBreathsPM, numberOfBreaths);

	if (validNBreaths != -1) {
		conf.breathsPerMinute = validNBreaths;
		HWSERIAL.println("BreathesPM OK");
	}



}

void setMotionLengthParam(long mLength) {

	long validMLength = hardLimiter(minMotionLength, maxMotionLength, mLength);

	if (validMLength != -1) {
		conf.motionLength = validMLength;
		HWSERIAL.println("MotionLength OK");
	}

}

void setInhaleExhaleRateParam(int rate) {

	int validRate = hardLimiter(minInhaleRatio, maxInhaleRatio, rate);

	if (validRate != -1) {
		conf.inhaleExhaleRatio = validRate;
		HWSERIAL.println("IE Ratio OK");
	}

}


void setAirVolParam(int rate) {

	int validRate = hardLimiter(minAirVol, maxAirVol, rate);

	if (validRate != -1) {
		conf.airVol = validRate;
		HWSERIAL.println("AirVolume Param OK");
	}

}


int switchPressed() {

	int pressedCount = 0;

	for (int i = 0; i < 100; i++) {

		if (digitalRead(ZERO_POS)) {

			pressedCount += 1;


		}

		if (pressedCount > 99) {

			return 1;

		}

		delay(1);

	}

	return 0;

}


void homeSwitchCheck() {

	unsigned long beforePressingTime = millis();

	while (switchPressed()) {

		unsigned long currentMillis = millis();

		if (currentMillis - beforePressingTime > 100) {

			//Serial.println("This is a valid press");

			zeroed = false;
			//Serial.println("Switch Pressed");
			break;
		}

	}

}

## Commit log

2020-03-25 First commit
    The software is done for debugging more, is not using controls a medic would use for breaths per minute etc.. planning to build a proper user interface
    [BagSupport1.SLDPRT, BagSupport2.SLDPRT, Base.SLDPRT, DIP SWITCH, SMAKN TB6600 STEPPER MOTOR DRIVER.SLDPRT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]
2020-03-25 Added STL Files
    [BagSupport1.STL, Base.STL, DisplayLid.STL, GearSupport.STL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]
2020-03-26 Made the base middle hole larger, it was cumbersome to mount the belt
    [Base.SLDPRT]
2020-03-26 Replaced gear belt tensioner with bearings and a screw
    [Base.SLDPRT, GearSupport.SLDPRT, RoulmentBeltTensing.SLDPRT]
2020-03-27 Added the controller for teensy 3.2
    The new controller support uart (Serial) commands formatted in Json like {"breathsPerMinute":12, "airVol":600, "ieRate":2}
    I have also designed a venturi tube that's going to be used for volume measurement.
    [VenturyTube.SLDPRT, VenturyTube.STL]
2020-03-29 added python interface
    [VenturyTube.SLDPRT, VenturyTube.STL]
2020-03-30 Changed the stepper library to have better control of the stepper
2020-03-30 Updated files to use nema 34 in the design
    [Base.SLDPRT, GearSupport.SLDPRT, MotorSupportNema34.SLDPRT, MotorSupportNema34.STL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]
2020-04-01 Added gerber files of the new board and redesigned a bit
    [Aluminium Gear re.SLDPRT, Aluminium Gear re.STL, Aluminium Gear re_tensioner.SLDPRT, Aluminium Gear re_tensioner.STL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]
2020-04-03 Worked on some connection pieces
    [23mm-to-16mm-hose adapter.SLDPRT, 23mm-to-16mm-hose adapter.STL, 90DegElbow_01.SLDPRT, 90DegElbow_01.STL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]
2020-04-03 Modified Pusher files
    [Base.SLDPRT, BeltGrabber.SLDPRT, BeltGrabber.STL, ICUVent.SLDASM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]
2020-04-04 Updated the bearings
    [ICUVent.SLDASM, Long_SC8UU.STL, SC8UU.SLDPRT]
2020-04-05 Added params for the nema 34 motor and 18 teeth gear
2020-04-06 Added step files, python interface is still WIP
    [Aluminium Gear re.SLDPRT, Aluminium Gear re.STEP, Aluminium Gear re_tensioner.STEP, BagSupport1.STEP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]
2020-04-06 Solved character issue, added a ambu grabber part
    [AmbuGrabber.SLDPRT, AmbuGrabber.STL, ICUVent.SLDASM, ambubag.SLDPRT]
2020-04-08 updated readme and added libraries
    [BackAccessHole.DXF]
2020-04-09 Added IGS files
    [Aluminium Gear re.IGS, Aluminium Gear re_tensioner.IGS, AmbuGrabber.SLDPRT, BagSupport1.IGS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]
2020-04-10 Added IGS files for tubes
    [23mm-to-16mm-hose adapter.IGS, 90DegElbow_01.IGS, ICUVent.SLDASM, OutputConnector-Nut.IGS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]
2020-04-11 Locked bar in place with a mirrored rod holder
    [AmbuGrabber.SLDPRT, Base.DXF, Base.SLDPRT, ICUVent.SLDASM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]
2020-04-16 Added connection elements
    [23mm-to-16mm-hose adapter.SLDPRT, 23mm-to-16mm-hose adapter.STL, 90DegElbow_02.SLDPRT, 90DegSuprapressure_Connector.SLDPRT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]
2020-05-15 Added a check for pressed switch
    [23mm-to-16mm-hose adapter.SLDPRT, 23mm-to-16mm-hose adapter.STL, 90DegElbow_02.STL, 90DegSuprapressure_Connector.SLDPRT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]

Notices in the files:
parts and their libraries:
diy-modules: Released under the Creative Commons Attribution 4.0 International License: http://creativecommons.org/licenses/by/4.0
